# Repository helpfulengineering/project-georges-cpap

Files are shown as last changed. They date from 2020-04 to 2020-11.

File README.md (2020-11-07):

# Georges CPAP
Plastic CPAP system with no moving parts.

# [Current Documentation](https://helpfulengineering.github.io/project-georges-cpap/)
Files in this repository are mainly for archival purposes + documentation. Source files are available [here](https://cad.onshape.com/documents/fcc843822e3f2cb218bbe91c/w/738c68d83bd9079113df055c/e/e5dcf7b0527b1f57e8a51f64?configuration=barb_id%3D0.003%2Bmeter%3Bchamber_width%3D0.003%2Bmeter%3Begress%3D4.0E-4%2Bmeter%3Bpatient_channel_diameter%3D0.005%2Bmeter%3Btext_depth%3D3.0E-4%2Bmeter%3Bwall_thickness%3D0.002%2Bmeter)

> #### Lowest O2 consumption rate of any CPAP system
> * Only 15-30L/min flow rate for 3.5-10cmH2O
>
> #### Doesn't require a flow generator
> * Eliminates investment in capital equipment and repair
> * Only needs an O2 source and a flowmeter
>
> #### Completely open airway
> * Eliminates re-breathing
> * Reduces risk of barotrauma
> * Decreases the work of breathing
> * Accomodates patient's high peak inspiratory flow demand
> * Allows use of suction catheter or bronchoscope without loss of CPAP
>
> #### Depends entirely on the O2 flow rate
> * Easily adjusts to patient's need (2.5-20cmH2O) simply by titrating O2 flow
> * PEEP adjustable by changing flow rate, without needing an additional valve
> 
> #### Complete, portable, single use system
> * CPAP set up in less than 2 minutes
> * Weighs only 10 grams and is 2" long
> * Permits CPAP without interruption during transport

## :vertical_traffic_light: [Project status](https://github.com/0x2b3bfa0/project-georges-cpap/projects/1)
*Note: actually being tracked through [GitHub Projects](https://github.com/0x2b3bfa0/project-georges-cpap/projects/1)*; follow the link to get a better view of the project status.
* [x] **Design**
* [x] **Prototyping**
* [ ] [**Calibration**](https://github.com/0x2b3bfa0/project-georges-cpap/issues/1)

## :gear: Manufacturing

### Mask Body
* Machine: Ender3 Pro
* Nozzle size: 0.4 mm
* Layer height: 0.28 mm
* Support: only for the protruding tubes.
* Notes for the mask: use variable layer height to print the valve section at 0.15 mm, and the rest at 0.4 mm for speed.

### Valve
* Machine: Anycubic Photon S
* Exposure: 3s
* Resin: basic

### Notes

* We're using the Montana Mask as the basis, but @aleksclark is terrible at freecad, so if you have to tweak the mask parameters, you'll need to trim off the excess of the strap anchors using the defeaturing tool
* It should be possible to add a biofilter to this design, see above for why it's not done yet

<!--
## Inspiration
After seeing that most of the recently designed ventilators were BVM-based and faced many manufacturing challenges that diminished their scalability, I've started to search better alternatives comprising non-invasive continuous ventilation, which [seemed to be a good idea](https://www.who.int/docs/default-source/coronaviruse/clinical-management-of-novel-cov.pdf). Fortunately, I found that some Spanish hospitals were using [a compact, commercial and medically-tested CPAP device](https://www.vygon.com/catalog/vygon-boussignac-cpap_572_00557013) that was really successful for the treatment of patients with mild/medium respiratory symptoms and didn't rely on electricity.

Though the working mechanism of this device was initially [patented](https://patents.google.com/patent/EP0978291B1/en) by its inventor (Georges Boussignac), the patents expired a year ago and everybody was free of replicating it, so the next obvious step was creating an open-source hardware alternative that could be readily mass-manufactured in this emergency situation.

## What it does
This device, consists only of a cleverly designed plastic piece that, when connected to a pressurized oxygen (or medical air) input, is able to deliver a continuous air flow to the patient without obstructing the airways. The *virtual valve*, formed by a radial laminar flow, allows the patients' lungs to keep a (selectable) minimum pressure as if the circuit had attached a mechanical PEEP valve, but allowing the patient to breathe freely in case of failure.

## What it doesn't do
This device doesn't filter the expiration air, but it has standard connections for medical-grade respiratory filters or, optionally, for 3M particulate filters (as last resort).

## Advantages
> #### Lowest O2 consumption rate of any CPAP system
> * Only 15-30L/min flow rate for 3.5-10cmH2O
>
> #### Doesn't require a flow generator
> * Eliminates investment in capital equipment and repair
> * Only needs an O2 source and a flowmeter
>
> #### Completely open airway
> * Eliminates re-breathing
> * Reduces risk of barotrauma
> * Decreases the work of breathing
> * Accomodates patient's high peak inspiratory flow demand
> * Allows use of suction catheter or bronchoscope without loss of CPAP
>
> #### Depends entirely on the O2 flow rate
> * Easily adjusts to patient's need (2.5-20cmH2O) simply by titrating O2 flow
> * PEEP adjustable by changing flow rate, without needing an additional valve
> 
> #### Complete, portable, single use system
> * CPAP set up in less than 2 minutes
> * Weighs only 10 grams and is 2" long
> * Permits CPAP without interruption during transport

## How I built it
The prototypes were 3D-printed under lockdown with the following setup:

> * Machine: Ender3 Pro
> * Nozzle size: 0.4 mm
> * Layer height: 0.28 mm
> * Support: only for the protruding tube.

Nevertheless, they were designed with injection molding in mind.

## Challenges I ran into
* Laminar flow imperfections: FDM prints have slight imperfections that keep the device from creating a good laminar flow, but this doesn't seem to affect the performance of the device.
* Lack of proper pressure tests: the prototypes were developed **under lockdown** and without access to pressurized air for testing, so they had to be tested with water and in precarious conditions.
* Forming a team: finally I couldn't find any team members because I needed very specific skills (like CFD) and this platform isn't good at all matching people for engineering projects; from the 10 requests I sent, I had zero answers.
* Promoting the idea: my video editing, technical writing and marketing skills are subpar.

## Accomplishments that I'm proud of
* The device prototype was tested with the shower hose and a glove as a test lung, with extremely successful results: a maximum output pressure of **20 cmH2O** with a maximum input flow rate of **4.25 litres per minute**, and these parameters can be tuned by adjusting the shape of the device.
* This project includes an OpenSCAD library of parametric pneumatic conical fittings as per **ISO5356-1** that can be useful in dozens of other projects which need to interact with ventilator components.
* Some of the latest iterations of the device were designed with injection molding in mind, so they can be mass-produced in a pretty scalable fashion.

## What I learned
Lots of things, in many different fields: from fluid dynamics to constructive solid geometry.

## What's next for Georges CPAP
* Run proper air-based artificial lung tests and a computer-based fluid simulation with OpenFOAM.
* Use the aforementioned tests to optimize the device calibration and mass-manufacture it through injection molding.

## License
[**CERN-OHL-P**](https://ohwr.org/project/cernohl/wikis/Documents/CERN-OHL-version-2)

<!--
## Rant
I don't speak hackathonese, and this project's video simply shows the device working without bells nor whistles. Please take in account that my marketing/branding skills are nonexistent and my team search was unsuccessful.
-->
-->

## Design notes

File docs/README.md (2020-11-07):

# Georges CPAP

```danger
DISCLAIMER: THIS IS NOT A MEDICAL DEVICE. These designs and documents are for experimental purposes ONLY and no warranty as to fitness or function is provided. The pressures created by this device are DANGEROUS and can cause barotrauma (i.e. lungs go POP, you go PLOP).
```

This fully printable device with no moving parts is able to provide a continuous positive pressure to a patient's airways while letting them breathe freely.

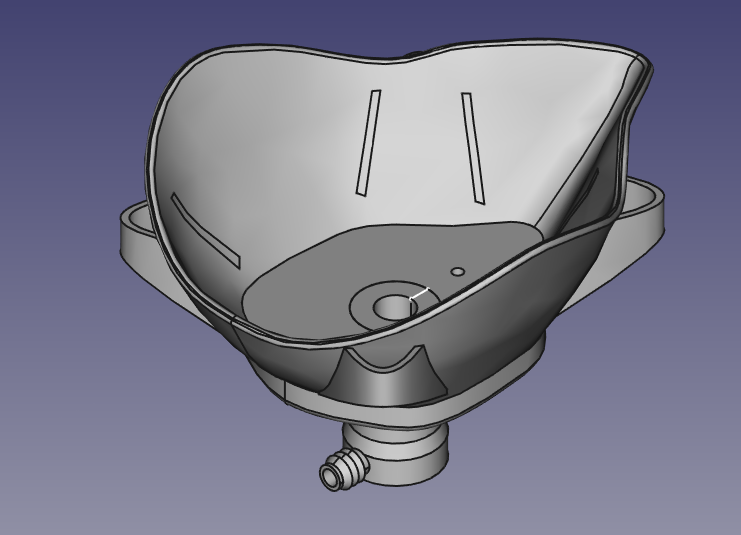
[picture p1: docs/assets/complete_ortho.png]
complete orthographic view


## About the device
This design provides a 3d-printable CPAP mask that can be manufactured in areas without access to standard CPAP or BiPAP equipment that has been shown to be desireable in COVID-19 patients [(source)](https://www.ncbi.nlm.nih.gov/pmc/articles/PMC7261654/).

This device is not suitable for mass-manufacture, entities with the resources and logistics necessary should purchase either commercial electronic BiPAP or CPAP machines, or the Boussignac CPAP produced by [VYGON](https://www.vygon.com/).

## Rudimentary Spanish Instructional Video

<iframe width="560" height="315" src="https://www.youtube.com/embed/moMq4IQBIsA" frameborder="0" allow="accelerometer; autoplay; clipboard-write; encrypted-media; gyroscope; picture-in-picture" allowfullscreen></iframe>

## Files

Source files have all been generated in OnShape, as a public document. The source files may be found [here](https://cad.onshape.com/documents/fcc843822e3f2cb218bbe91c/w/738c68d83bd9079113df055c/e/e5dcf7b0527b1f57e8a51f64?configuration=barb_id%3D0.003%2Bmeter%3Bchamber_width%3D0.003%2Bmeter%3Begress%3D4.0E-4%2Bmeter%3Bpatient_channel_diameter%3D0.010%2Bmeter%3Btext_depth%3D3.0E-4%2Bmeter%3Bwall_thickness%3D0.002%2Bmeter). The design is parametric, so you may desire to tune the values to achieve different goals. The main parameter that users will want to tune is 'patient channel diameter', but the 'egress' parameter may also be tuned to account for differences in SLA exposure, resins, and finishing processes.

| Item |
| ---- |
| [Mask](assets/CPAP Mask.stl) |
| [10mm Valve](assets/cpap_valve_10mm.stl) |
| [9mm Valve](assets/cpap_valve_9mm.stl) |
| [8mm Valve](assets/cpap_valve_8mm.stl) |
| [7mm Valve](assets/cpap_valve_7mm.stl) |
| [6mm Valve](assets/cpap_valve_6mm.stl) |
| [5mm Valve](assets/cpap_valve_5mm.stl) |

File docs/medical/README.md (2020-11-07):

# Medical
```danger
DISCLAIMER: THIS IS NOT MEDICAL ADVICE. This is just some interesting data that real doctors may be referred to in order to inform their treatment decisions
```

## When to implement CPAP treatment
This article has a useful algorithm to make decisions about the use of CPAP treament in COVID-19 patients, including considerations of FiO2 and other patient parameters.
[https://www.medrxiv.org/content/10.1101/2020.06.05.20123307v1.full.pdf](https://www.medrxiv.org/content/10.1101/2020.06.05.20123307v1.full.pdf)

## Effectiveness
Article with information about the effectiveness of CPAP therapy in COVID-19 patients
[https://www.medrxiv.org/content/10.1101/2020.06.05.20123307v1.full.pdf](https://www.medrxiv.org/content/10.1101/2020.06.05.20123307v1.full.pdf)

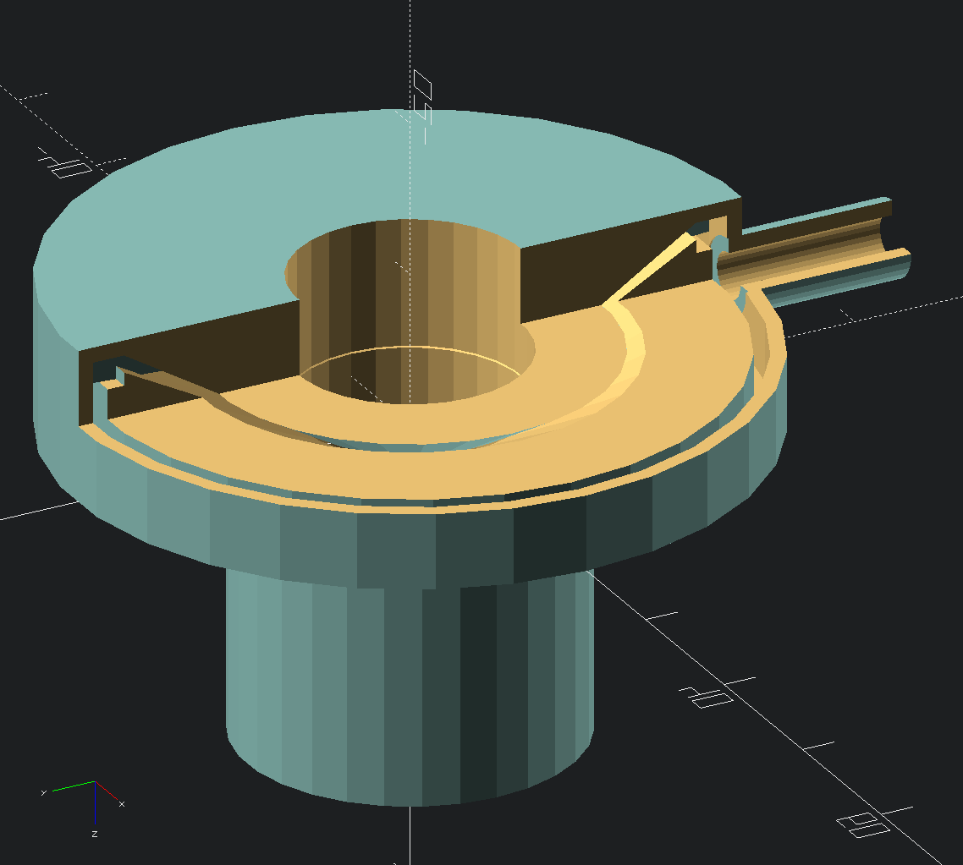
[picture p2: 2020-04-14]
documentation/images/support.png

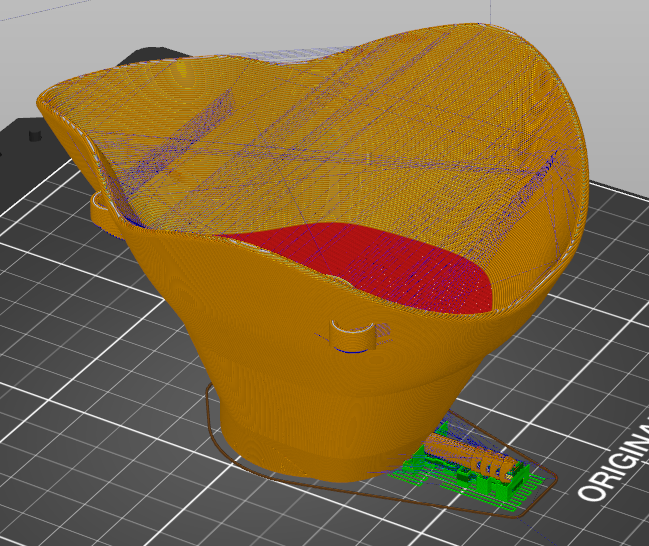
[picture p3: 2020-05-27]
documentation/images/mask.png

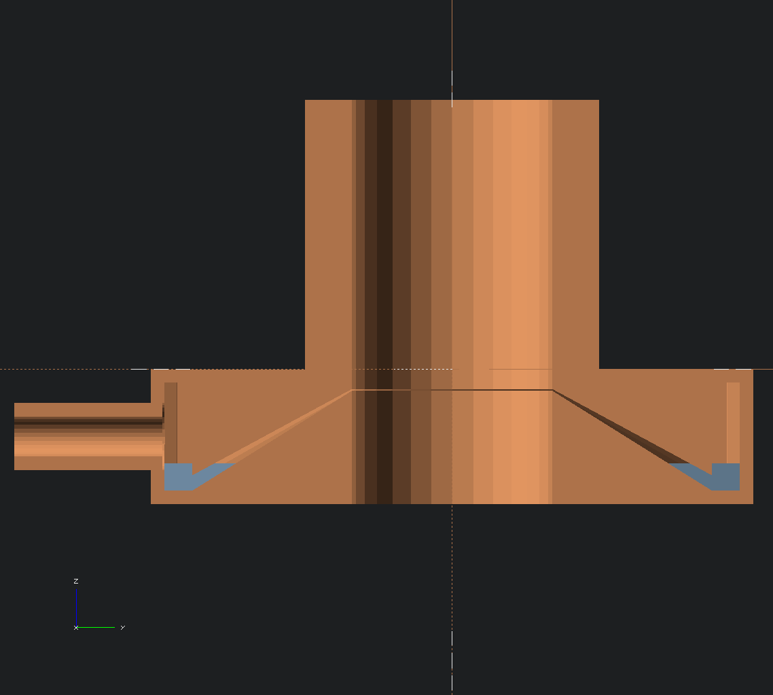
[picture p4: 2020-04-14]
documentation/images/cross-section.png

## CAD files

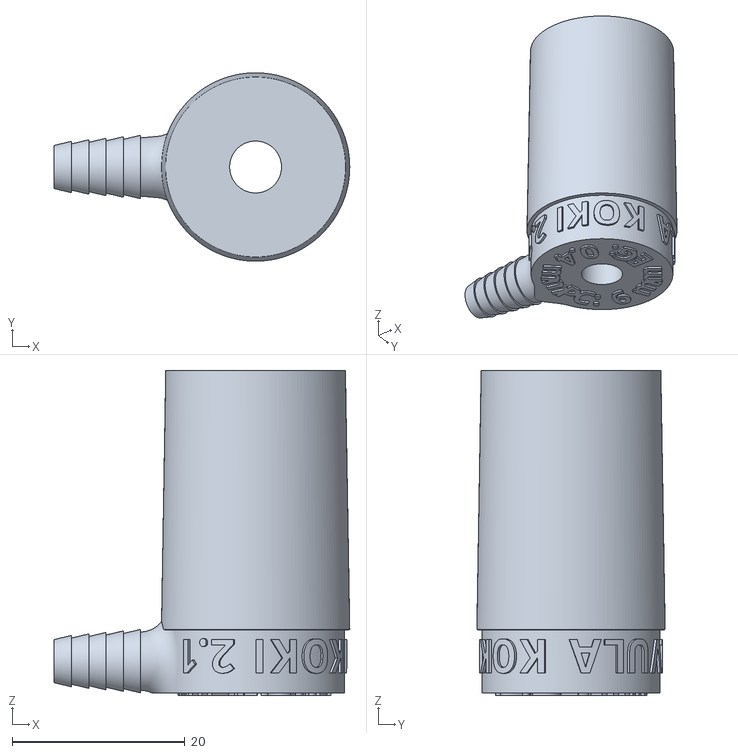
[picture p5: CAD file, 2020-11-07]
docs/assets/cpap_valve_6mm.stl
34.2 x 21.8 x 37.6

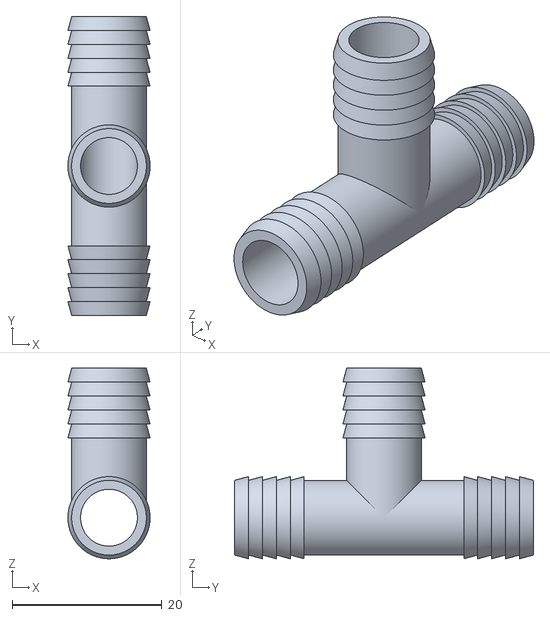
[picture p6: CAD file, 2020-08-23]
test_articles/tee.stl
11.0 x 40.0 x 25.5

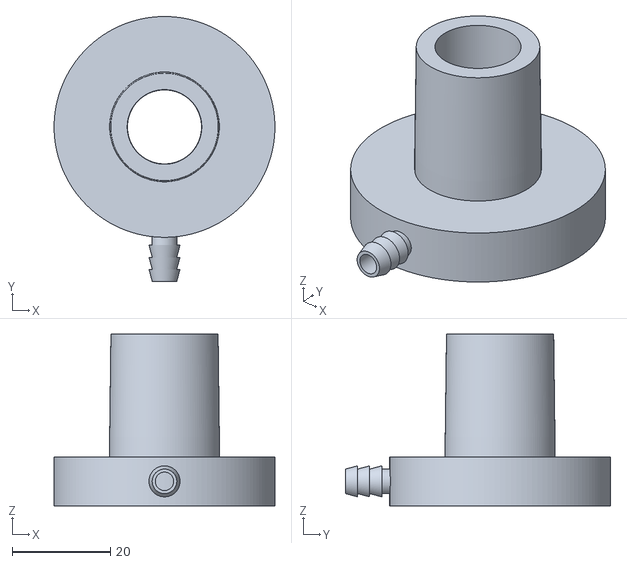
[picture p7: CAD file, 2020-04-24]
valve.stl
45.0 x 54.0 x 35.0

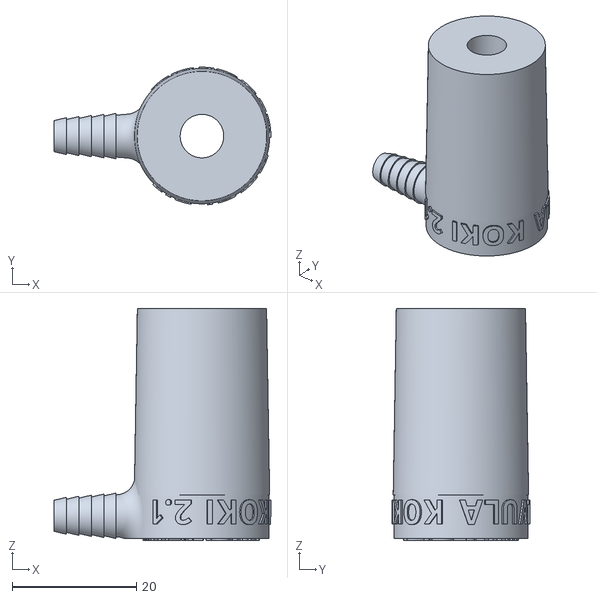
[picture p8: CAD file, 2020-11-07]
docs/assets/cpap_valve_7mm.stl
34.9 x 22.2 x 37.3

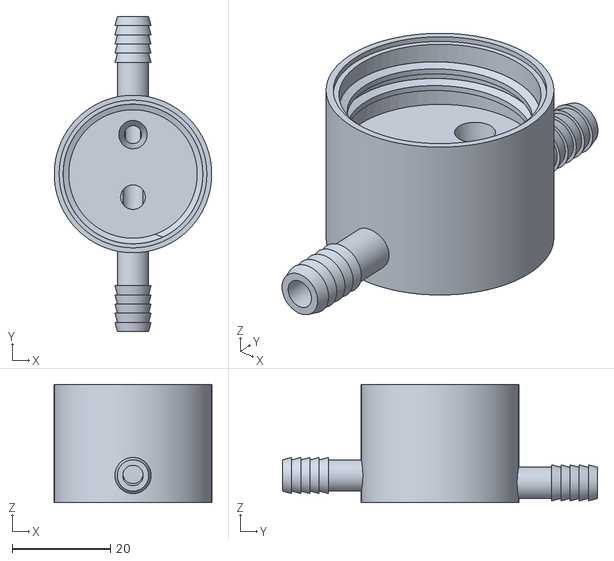
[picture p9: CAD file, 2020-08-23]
test_articles/bottle_cap_fitting.stl
32.0 x 64.0 x 24.0

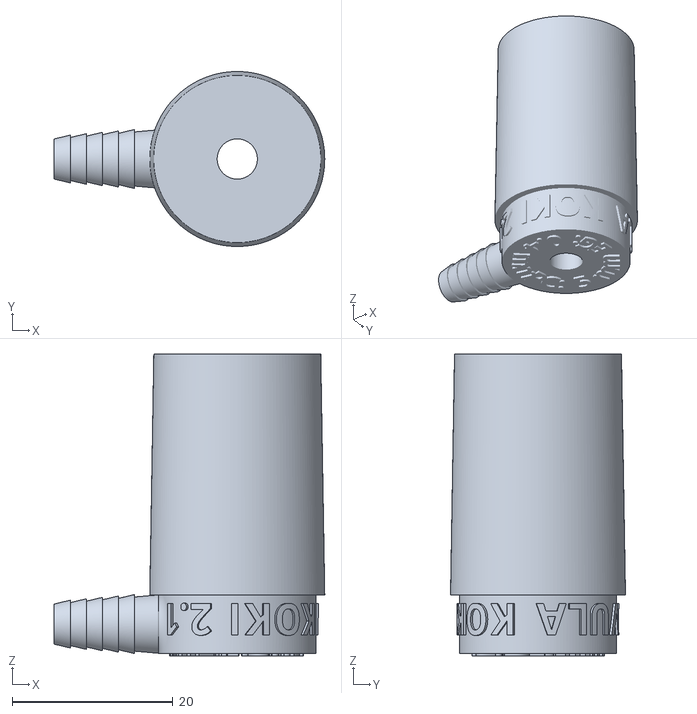
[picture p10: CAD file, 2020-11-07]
docs/assets/cpap_valve_5mm.stl
33.7 x 21.8 x 37.6

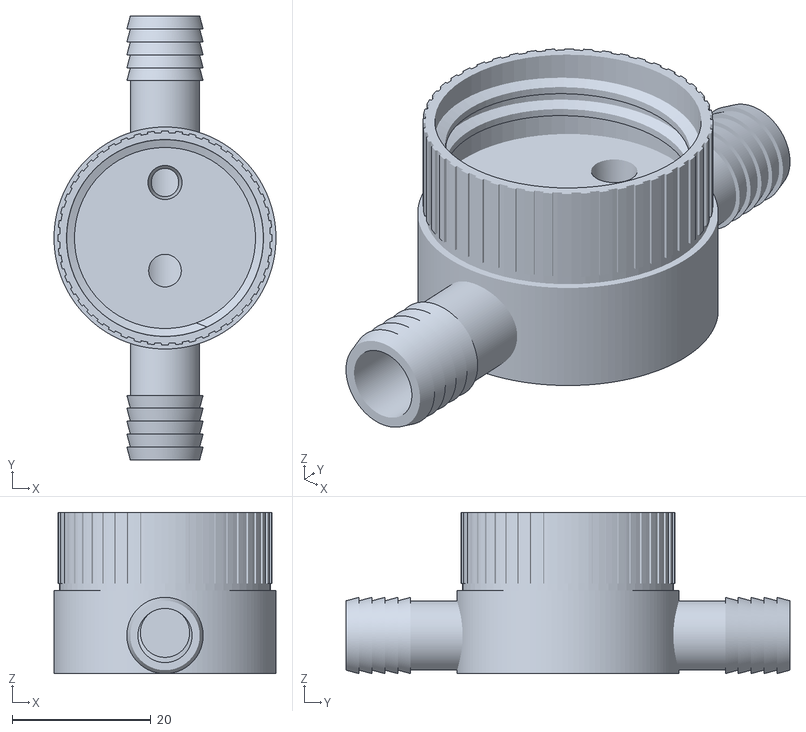
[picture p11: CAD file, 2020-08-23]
test_articles/bottle_cap_fitting_2.stl
32.0 x 64.0 x 23.2

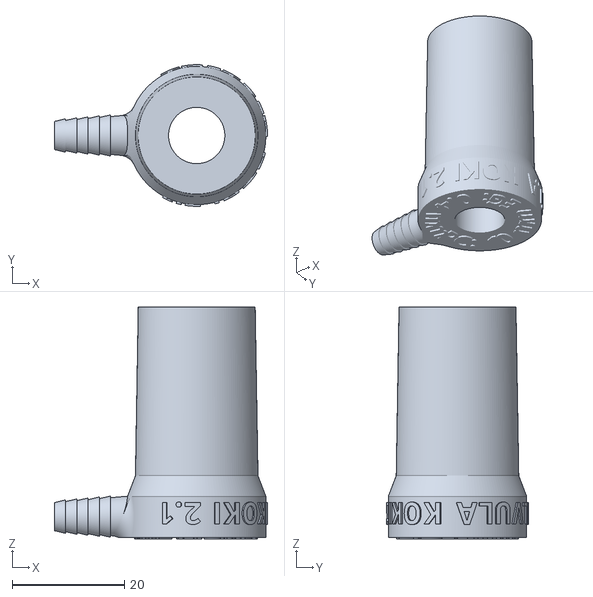
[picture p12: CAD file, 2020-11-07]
docs/assets/cpap_valve_10mm.stl
37.9 x 25.2 x 41.3

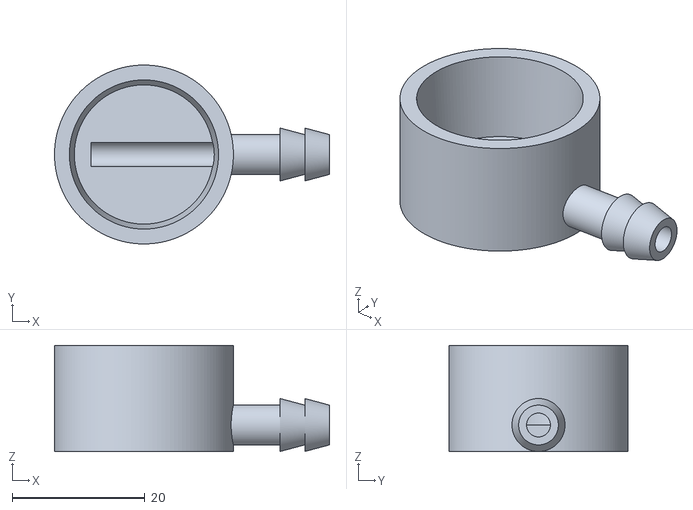
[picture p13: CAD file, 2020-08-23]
test_articles/sink_adapter.stl
41.5 x 27.0 x 16.0

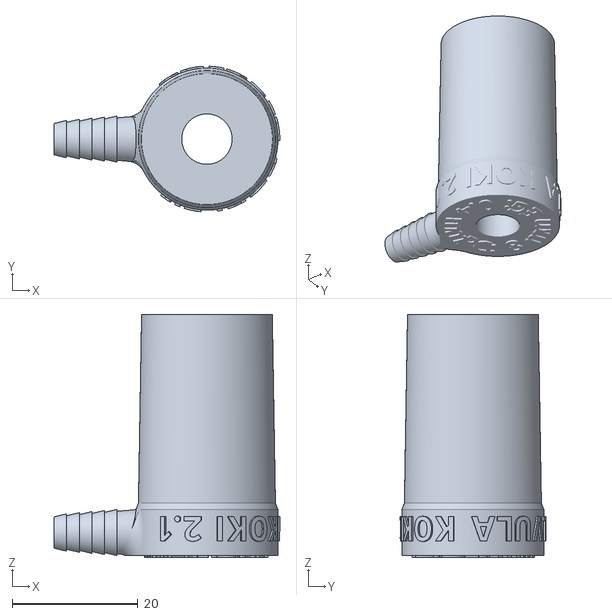
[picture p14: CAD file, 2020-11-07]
docs/assets/cpap_valve_8mm.stl
35.9 x 23.2 x 38.6

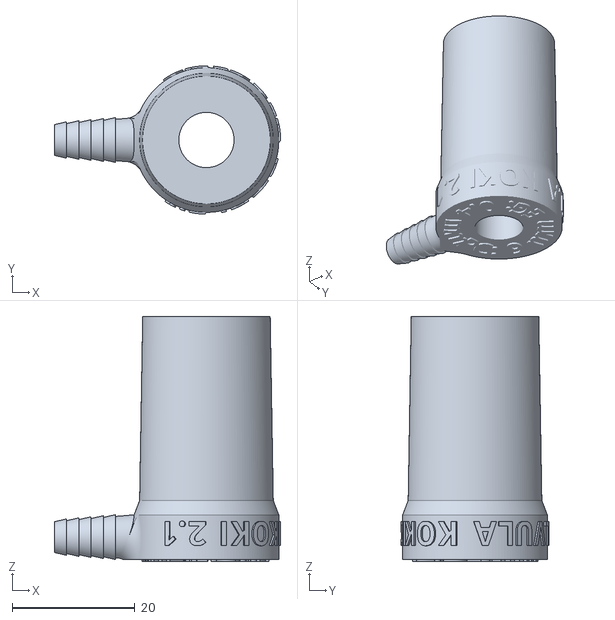
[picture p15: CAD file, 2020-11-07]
docs/assets/cpap_valve_9mm.stl
36.9 x 24.2 x 40.0

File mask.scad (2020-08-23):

/*
 * Model: pneumatic CPAP with no moving parts, mask included.
 *
 * Copyright (C) 2020 Helio Machado <0x2b3bfa0@googlemail.com>
 *                    Aleks Clark   <aleks.clark@gmail.com>
 *
 * This code describes open hardware and is licensed under the CERN-OHL-P V2.
 *
 * You may distribute, modify and materialize these designs as long as you do
 * it under the terms of the CERN-OHL-P V2 license (https:/cern.ch/cern-ohl).
 * This documentation is distributed WITHOUT ANY EXPRESS OR IMPLIED WARRANTY,
 * INCLUDING OF MERCHANTABILITY, SATISFACTORY QUALITY AND FITNESS FOR A GIVEN
 * PURPOSE.
 *
 * Please refer to the accompanying CERN-OHL-P V2 license text for a detailed
 * description of the applicable conditions.
 */

use <library/primitives/tube.scad>;
use <library/connectors/conical/ISO5356_1.scad>;
use <library/valves/georges.scad>;
use <library/connectors/hose/barb.scad>;

$fn=128;  // Face number: 128 for quality, 16 for speed.


module valve() {
    georges(
        diameter=[40, 15],
        length=18,
        wall=2,
        barb=[10, 30, 0.66, 20],
        channel=0.4,
        angle=35
    );
}


module mask() {
    difference() {
        union() {
            difference() {
                translate([-110.1, -101.9, 25]) import("library/masks/montana/body.stl");
                translate([-50, -50, -65]) cube([100, 100, 100]);
            }
            translate([0, 0, 35]) rotate([0, 180, 180]) {
                linear_extrude(35, convexity=10, scale=[0.6, 0.64]) {
                    import("library/masks/montana/adaptor.svg", center=true);  
                }
            }
        }
        cylinder(18, d=40);
        cylinder(38, d=15);
        translate([0, -15, 5.66]) rotate([90, 0, 0]) cylinder(35, d=10);
        translate([0, 25, 2]) cylinder(35, d=5);
        translate([0, 26, 4]) rotate([270, 0, 0]) cylinder(35, d1=5);
    }
}


difference() {
    union() {
        mask();
        valve();
        difference() {
            translate([0, 26, 4]) rotate([270,0,0]) barb(6.35, 20, clearance=10, wall=1.2, barb=0.5);
            translate([0, 25, 2]) cylinder(35, d=5);
        }
    }
    // cut off the bottom of the barb for ease of printing
    translate([0, -50, -1.5]) cube([50, 150, 100]);
}

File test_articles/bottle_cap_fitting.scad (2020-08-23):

/*
 * Model: pneumatic CPAP with no moving parts, mask included.
 *
 * Copyright (C) 2020 Helio Machado <0x2b3bfa0@googlemail.com>
 *                    Aleks Clark   <aleks.clark@gmail.com>
 *
 * This code describes open hardware and is licensed under the CERN-OHL-P V2.
 *
 * You may distribute, modify and materialize these designs as long as you do
 * it under the terms of the CERN-OHL-P V2 license (https:/cern.ch/cern-ohl).
 * This documentation is distributed WITHOUT ANY EXPRESS OR IMPLIED WARRANTY,
 * INCLUDING OF MERCHANTABILITY, SATISFACTORY QUALITY AND FITNESS FOR A GIVEN
 * PURPOSE.
 *
 * Please refer to the accompanying CERN-OHL-P V2 license text for a detailed
 * description of the applicable conditions.
 */

use <../library/connectors/hose/barb.scad>;
use <../library/connectors/bottle/necks_caps.scad>;

$fn=128;  // Face number: 128 for quality, 16 for speed.

difference() {
    union() {
        translate([0,0,12]) 28PCO1881();
        cylinder(12, d=32);
        translate([0, 7, 4]) rotate([270,0,0]) barb(6.35, 25, clearance=15, wall=1.1, barb=0.5);
        translate([0, -7, 5.5]) rotate([90,0,0]) barb(6.35, 25, clearance=15, wall=1.1, barb=0.5);
        translate([0,0,12]) difference() {
            cylinder(12, d=32);
            cylinder(12, d=30);
        }
    }

    translate([0,8,5.4]) cylinder(9, d1=3.5, d2=6);
    translate([0,6,4]) rotate([270,0,0]) cylinder(10, d=4.1);

    translate([0,-16,5.9]) rotate([270,0,0]) cylinder(14, d=4.1);
    translate([0,-4.7,5.99]) cylinder(8, d=5);
    
}
  

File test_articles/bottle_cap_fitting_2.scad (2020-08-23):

/*
 * Model: pneumatic CPAP with no moving parts, mask included.
 *
 * Copyright (C) 2020 Helio Machado <0x2b3bfa0@googlemail.com>
 *                    Aleks Clark   <aleks.clark@gmail.com>
 *
 * This code describes open hardware and is licensed under the CERN-OHL-P V2.
 *
 * You may distribute, modify and materialize these designs as long as you do
 * it under the terms of the CERN-OHL-P V2 license (https:/cern.ch/cern-ohl).
 * This documentation is distributed WITHOUT ANY EXPRESS OR IMPLIED WARRANTY,
 * INCLUDING OF MERCHANTABILITY, SATISFACTORY QUALITY AND FITNESS FOR A GIVEN
 * PURPOSE.
 *
 * Please refer to the accompanying CERN-OHL-P V2 license text for a detailed
 * description of the applicable conditions.
 */

use <../library/connectors/hose/barb.scad>;
use <../library/connectors/bottle/necks_caps.scad>;

$fn=128;  // Face number: 128 for quality, 16 for speed.

difference() {
    union() {
        translate([0,0,12]) 28PCO1881();
        cylinder(12, d=32);
        translate([0, 7, 5.5]) rotate([270,0,0]) barb(10, 25, clearance=15, wall=1.1, barb=0.5);
        translate([0, -7, 5.5]) rotate([90,0,0]) barb(10, 25, clearance=15, wall=1.1, barb=0.5);
    }

    translate([0,8,5.99]) cylinder(8, d1=3.5, d2=5);
    translate([0,6,5.5]) rotate([270,0,0]) cylinder(10, d=7.1);

    translate([0,-16,5.9]) rotate([270,0,0]) cylinder(14, d=7.1);
    translate([0,-4.7,5.99]) cylinder(8, d=4.7);

}
  

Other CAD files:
test_articles/sink_adapter.scad
test_articles/tee.scad

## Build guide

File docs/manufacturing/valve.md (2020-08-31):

# Valve

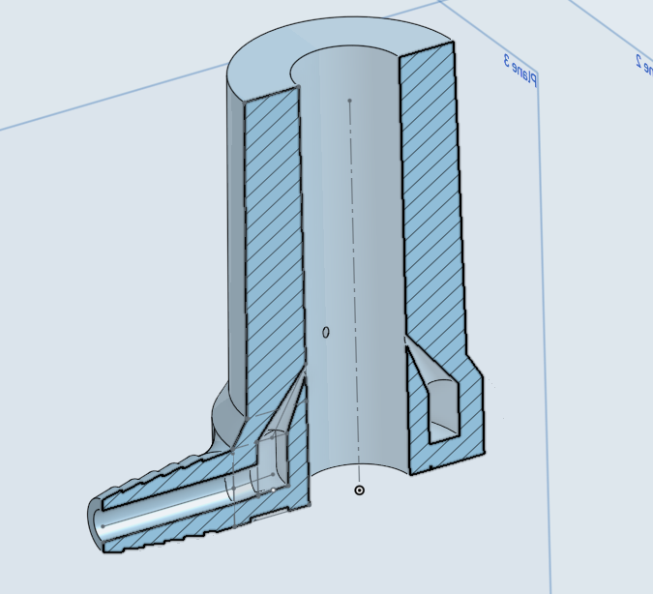
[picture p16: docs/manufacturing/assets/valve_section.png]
valve section view


The valve is designed to be printed using SLA printing. It's theoretically possible to achieve the required tolerances with FDM, but holding pressure at \~40 PSI is an additional challenge, easily met using SLA.

## Print Settings

In order to achieve the 0.4mm hole required to achieve the necessary airspeed, SLA exposure times will need to be reduced far below the defaults.

### AnyCubic Photon Z - "Basic" Resins

|-----------------|---------|
| Layer Thickness | 0.050mm |
| Normal Exposure | 3s      |
| Bottom Exposure | 60s     |

## Orientation / Supports

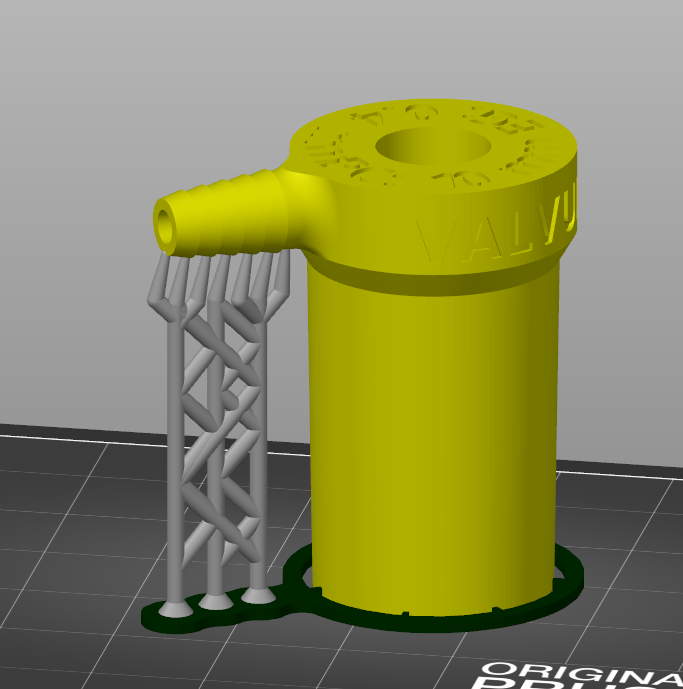
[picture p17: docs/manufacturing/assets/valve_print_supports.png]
valve with print supports


In order to minimize cleanup while preserving surface quality, it is recommended to print the valve with the barb attachment up, and generate supports for the barb. This also permits an increased print density when compared to an angled print.

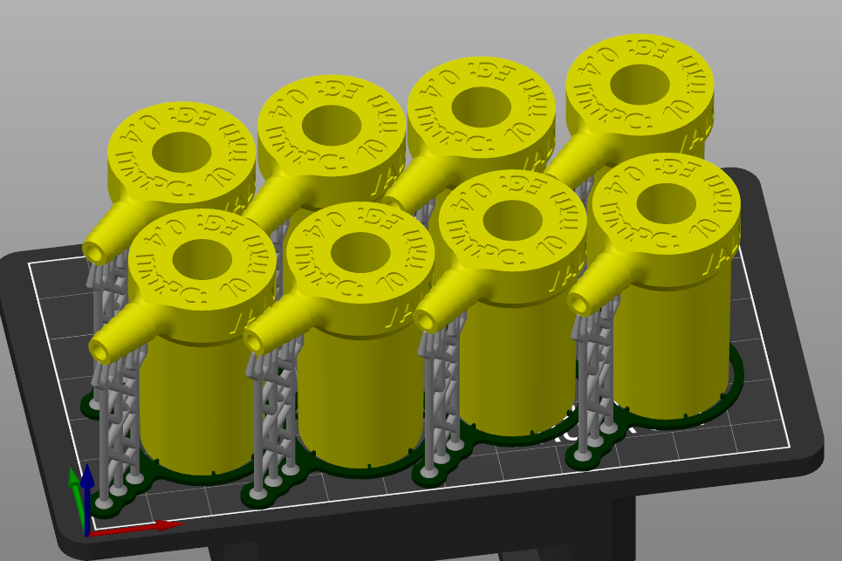
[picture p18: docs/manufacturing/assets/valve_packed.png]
valve packed


## Post-Processing

### Washing

To wash the part of uncured resin, and preserve IPA supplies, a 4-wash process is advised (left to right):

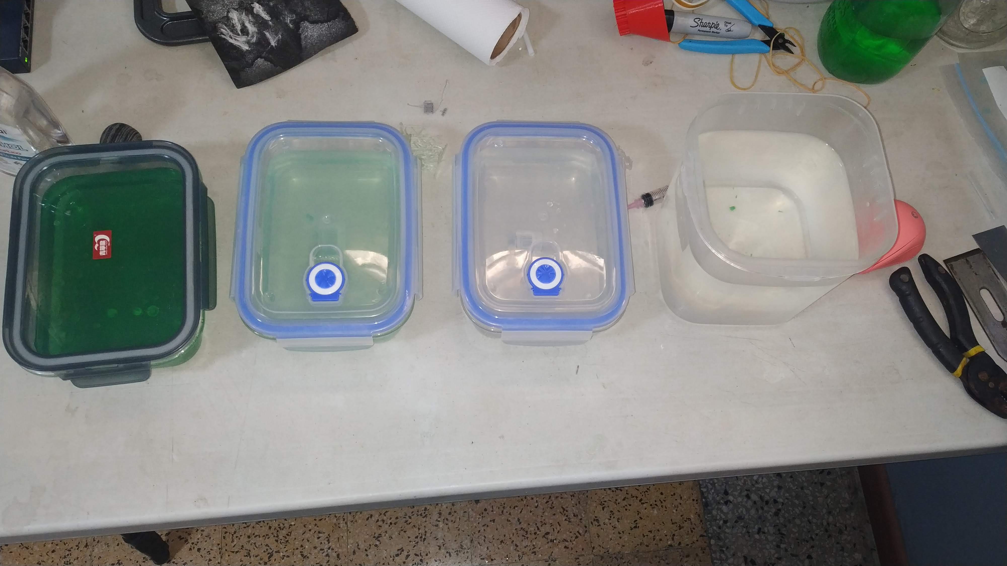
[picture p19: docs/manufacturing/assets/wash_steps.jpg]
washing steps


* Step 1: IPA - bulk resin removal - remove supports after this
* Step 2: IPA - resin removal
* Step 3: IPA - final resin removal
* Step 4: Water - IPA removal

In addition to the usual concerns with washing SLA parts, the internal cavity of the void must be flushed of uncured resin. This step is also useful to verify that none of the egress holes have clogged during printing.

Flushing should be performed at each stage of the washing process to ensure the internal cavity is fully clear of uncured resin.

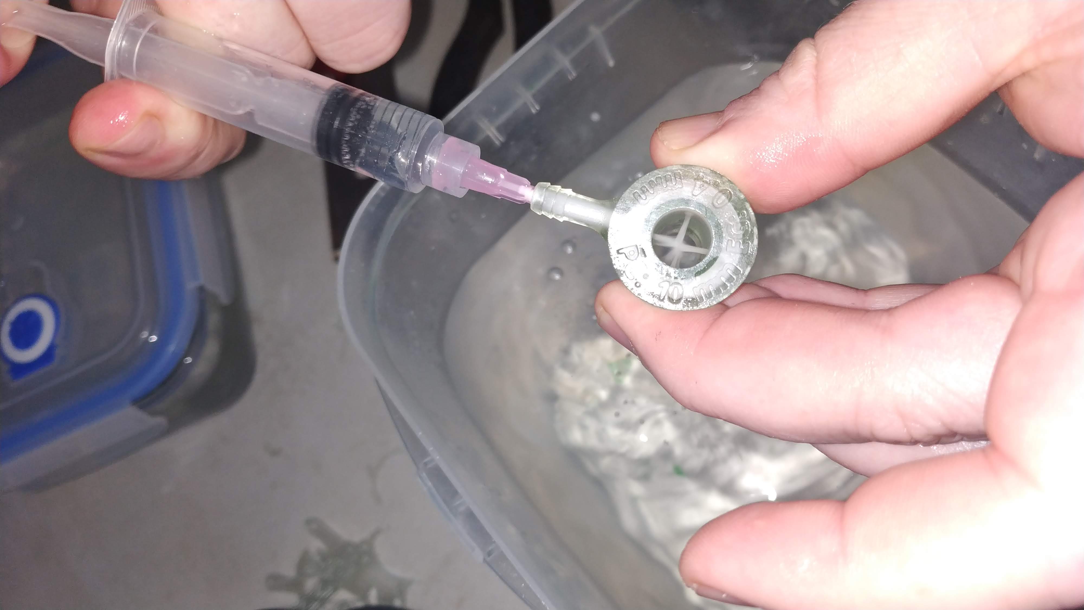
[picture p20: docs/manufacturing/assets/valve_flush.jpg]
valve flushed


### Curing

Due to the reduced exposure times in printing, it is recommended to double standard curing times to ensure a full cure, especially of the interior cavity.

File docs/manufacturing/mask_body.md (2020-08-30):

# Mask Body

The mask body can be printed using a standard FDM printer. The attachment points have a 30deg overhang, so your printer needs to be able to achieve this *somewhat* reliably.

## Supports
The only part that absolutely requires supports is the manometer port, but most slicers should allow you to select this portion for supports fairly easiy.
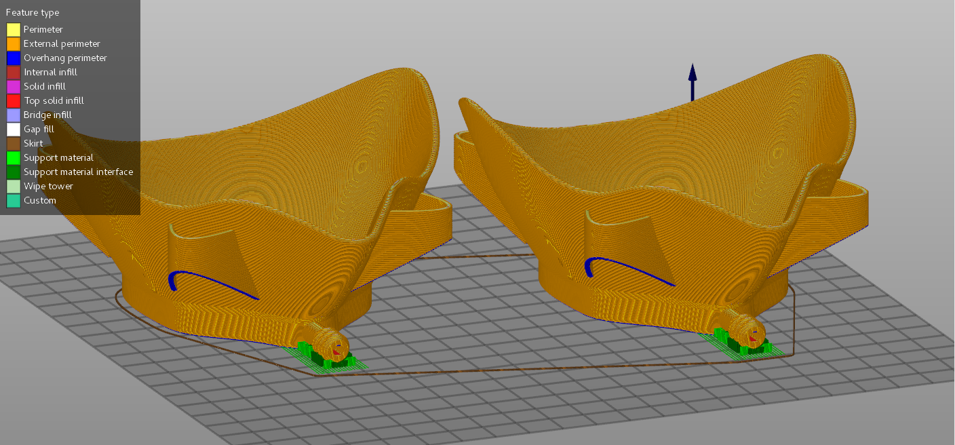
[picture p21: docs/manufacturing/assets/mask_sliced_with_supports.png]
Sliced with supports


## Materials

### Plastic
While PLA doesn't present a health hazard, it will be less durable in a medical environment due to the increased moisture it will absorb from the patient's breath. 

Ideally the mask should be printed in PETG or ABS.

### Gasket / Seal
The seal around the face is accomplished by applying self-adhesive weather stripping (burlete in Spanish) around the perimeter of the mask. This should be of the hollow variety that will provide comfort to the user.

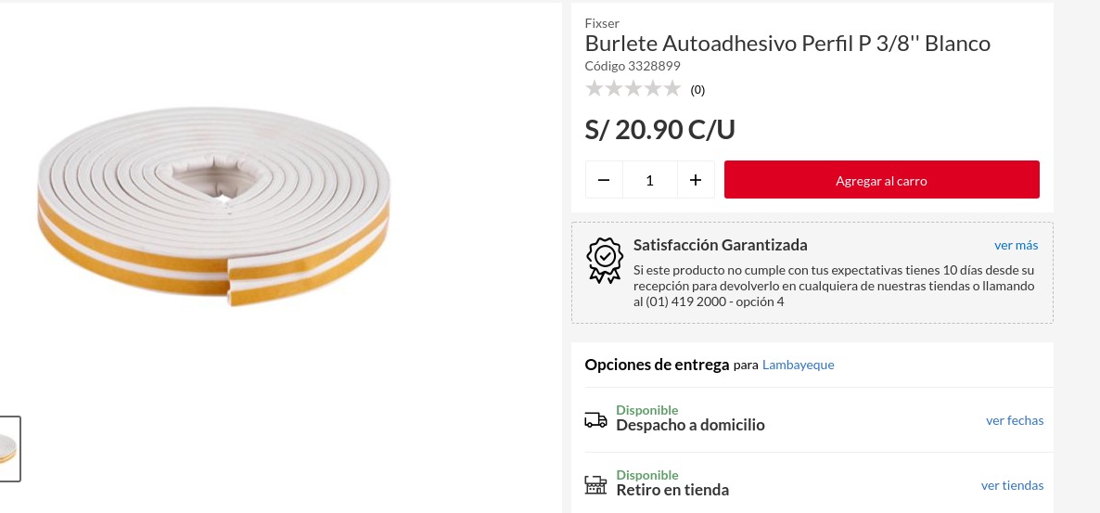
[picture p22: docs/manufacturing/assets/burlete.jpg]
burlete


The stripping should be applied as close to the edge of the mask as possible in order to provide a good seal. A double row is needed in the nose area.
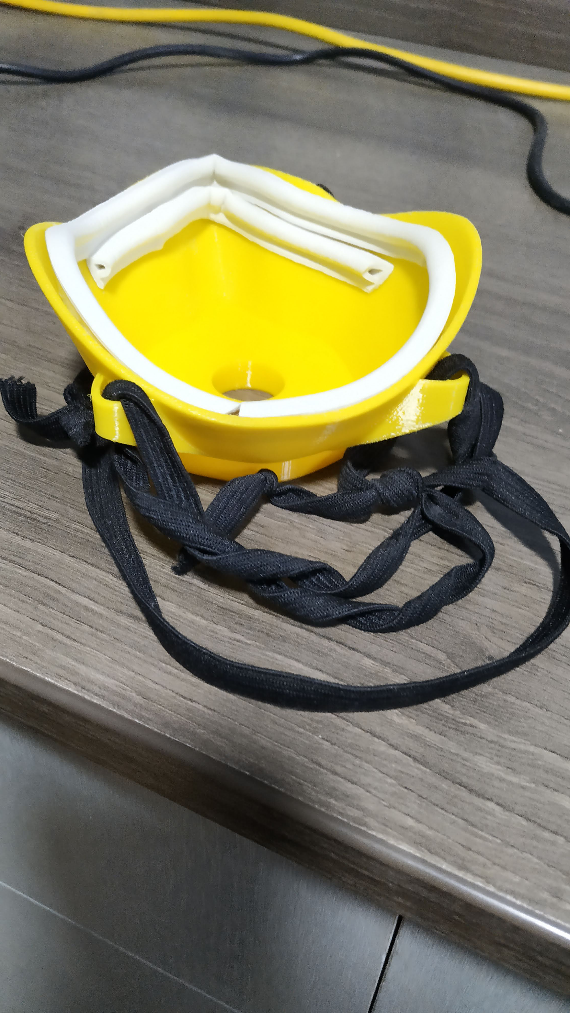
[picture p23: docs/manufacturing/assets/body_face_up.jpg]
mask body face up


### Banding
A doubled 1cm elastic band is *barely* sufficient to provide a decent seal. Research is needed into materials that are readily available, comfortable to wear for extended periods, and fairly higenic.

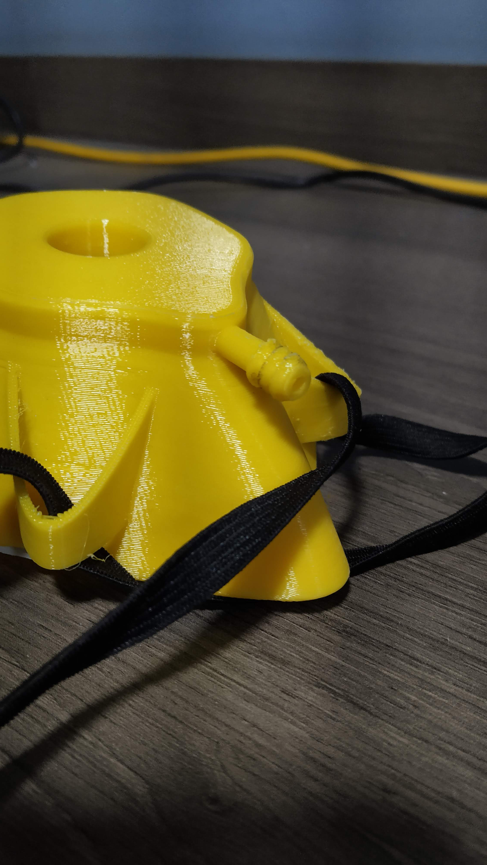
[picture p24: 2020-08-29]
docs/manufacturing/assets/body_port_detail.jpg

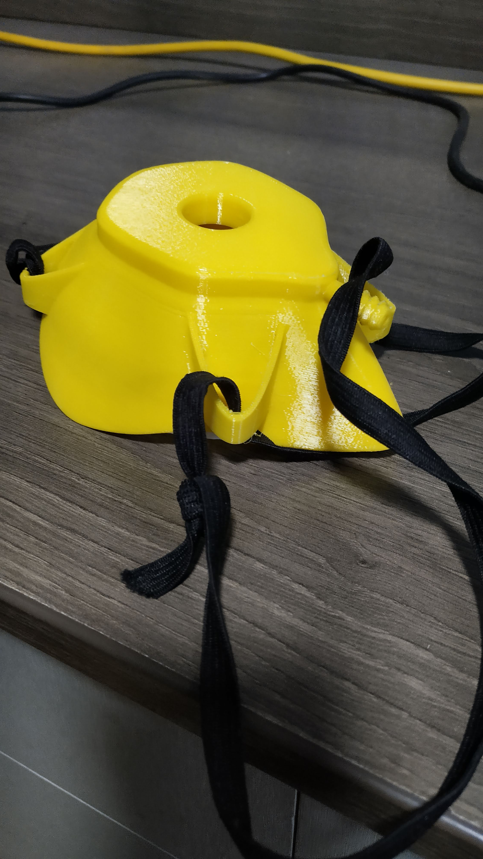
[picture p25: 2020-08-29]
docs/manufacturing/assets/body_face_down.jpg

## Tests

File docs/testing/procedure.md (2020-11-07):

# Procedure

Testing the valve is relatively simple, provided the necessary equipment is present. Two factors are highly important in testing and implementation:

## Pressure

Pressure and flow are interdependent, but the valve depends on pressure in order to generate the airspeed necessary to form the virtual valve. At the low flow present in medical equipment, even small leaks can result in pressure drops, so ensure that no leaks are present between the flow limiter and the valve. The valve's O2 port has been designed to accomodate standard oxigen line fittings with minimal leaks, but teflon tape may be used if leaks are present. 

## Flow

Standard air compressors have a much higher flow rate than medical equipment, so flow limiting is crucial. You may achieve good PEEP with your test equipment, then take it to the hospital and get terrible PEEP.

## Testing the valve

A video demonstrating testing is included below. TURN DOWN YOUR VOLUME
<iframe width="560" height="315" src="https://www.youtube.com/embed/-pk_lfGOONA" frameborder="0" allow="accelerometer; autoplay; clipboard-write; encrypted-media; gyroscope; picture-in-picture" allowfullscreen></iframe>

Connect a soda bottle to your manometer via any means available, and insert the valve into the mouth of the soda bottle. Some teflon tape may be necessary to achieve a good seal.

Valves come in a variety of channel diameters from 10mm to 5mm. These produce an increasing range of pressures. Depending on the calibration of your SLA printer, you may need to use a smaller channel to achieve your target pressure. The table below gives ballpark maximum pressures achievable with a well-calibrated printer

| Channel Diameter | Pressure (cm H2O) |
| ---------------- | ----------------- |
| 10mm             | 6-9cm             |
| 9mm              | 7-11cm            |
| 8mm              | 8-12cm            |
| 7mm              | 8-14cm            |
| 6mm              | 9-15cm            |
| 5mm              | 10-17cm           |

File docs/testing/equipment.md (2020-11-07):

# Equipment

Ideally, testing would be performed with a standard medical oxigen tank, regulator, and humidifier similar to this one:
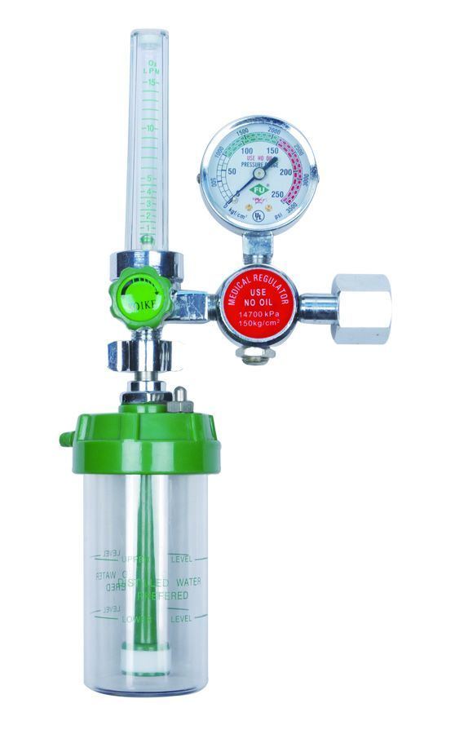
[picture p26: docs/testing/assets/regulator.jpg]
Oxigen equipment


In the absence of real equipment, the following may be substituted with care to match the characteristics of medical equipment.

## Air Supply

Air compressor with regulator, should be able to provide 15L/min @ 40 PSI

## Flow limiter

Pressure compensated, should be able to limit to 15L/min to match standard medical equipment. Can be approximated with an 0.8mm printer nozzle @ 35 PSI. [Calculator for airflow](https://www.tlv.com/global/TI/calculator/air-flow-rate-through-orifice.html)

To verify you're producing 15L/min, submerge a container of known volume in a large container of water. Place the air line (after the flow limiter) under the container and measure the amount of time it takes to make the container fill. E.G. with a 15L container that starts out completely full of water, the container should rise completely out of the water in about 1 minute, a 5L container should take 20 seconds. There is some wiggle room, but medical equipment is mostly limited to 15L, so accurate testing depends on accurate flow limiting.

## Manometer

A manometer that can accurately show pressures in the 0-20cm H2O range is vital. A U-tube manometer is easily constructed out of clear vinyl tubing. A printable manometer can be found [on thingiverse](https://www.thingiverse.com/thing:1205032)

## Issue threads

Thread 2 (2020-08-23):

### ISSUE TITLE
Laminar flow imperfections

### ISSUE THREAD

**Issue by 0x2b3bfa0** [helpfulengineering/project-georges-cpap#2]
FDM prints have slight imperfections that keep the inner channel's surface from creating a good laminar flow.

**Comment by 0x2b3bfa0** [comment]
This doesn't seem to pose any issue as per the empirical tests done in #1

**Comment by aleksclark** [comment]
This doesn't seem completely solved, in testing the mask produced by #6 I was not able to achieve more than 2cm H2O with air.
see: https://www.youtube.com/watch?v=yGmyCOS2pSA
https://www.youtube.com/watch?v=ehNEK6gB7iQ

**Comment by 0x2b3bfa0** [comment]
Referring to your water test, it looks like a small section of the channel is clogged. Might that affect the performance?

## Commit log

2020-04-11 Add the project files
    [boussignac.scad, boussignac.stl]
2020-04-11 Mirror (upside-down) for printing
    [boussignac.scad, boussignac.stl]
2020-04-12 Fix trigonometry errors
    [boussignac.scad, boussignac.stl]
2020-04-14 Improve the air flow
    [boussignac.scad, boussignac.stl]
2020-04-16 Add prototypes
2020-04-17 Move the #1 issue link to the calibration section
2020-04-24 Restructure the project
    [boussignac.scad, boussignac.stl, model.scad, model.stl]
2020-04-24 Fix obstruction
    [model.scad, model.stl]
2020-04-24 Fix input nozzle diameter
    [model.scad, model.stl]
2020-04-24 Fix input diameter
    [model.scad, model.stl]
2020-04-24 Adjust diameters
    [model.scad, model.stl]
2020-05-25 incorporate valve into montana mask
    [MontanaMaskFilterFrameWithFlange.stl, MontanaMasks_adaptor_slice.stl, mask_bottom.scad, mask_bottom.stl]
2020-05-25 fix some silly mistakes and also ensure wall width in original code
    [mask_bottom.scad, mask_bottom.stl]
2020-05-26 add aux port and 3mf
    [full_mask.3mf, mask_bottom.scad, mask_bottom.stl]
2020-05-27 Cleanup structure
    [MontanaMaskFilterFrameWithFlange.stl, MontanaMasks_adaptor_slice.stl, full_mask.3mf, mask.3mf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]
2020-05-27 Add printing recommendations
2020-05-29 Revert visual fixes 0.1 mm cause a huge impact in some tapered tubes.
2020-05-29 Simplify valve topology
    [mask.3mf, mask.scad, valve.scad, valve.stl]
2020-06-17 wip, needs cleanup
    [bottle_cap_fitting.scad, bottle_cap_fitting.stl, bottle_cap_fitting_2.scad, bottle_cap_fitting_2.stl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]
2020-06-18 mach valve
    [valve.FCStd, valve_mach.FCStd]
2020-08-16 clean up a lot of stuff, commit actual working valve
    [mask.3mf, valve.3mf, valve.step, valve_abrubt.stl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]
2020-08-23 clean some stuff up
    [valve.scad]
2020-08-23 clean up intermediate files
    [valve.FCStd, valve_mach.FCStd]
2020-11-07 update documentation to semi-final form
    [cpap_valve_10mm.stl, cpap_valve_5mm.stl, cpap_valve_6mm.stl, cpap_valve_7mm.stl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]
